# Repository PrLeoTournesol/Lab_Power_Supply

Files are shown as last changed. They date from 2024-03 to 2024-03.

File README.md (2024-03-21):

# Lab Power Supply

## Overview

The goal is to create an inexpensive laboratory power supply with stable voltage and medium/high current output. I will use an old but working power supply, the _API2PC23_ from IBM. Due to its peculiar shape, the 3D files I created might not be suited for every power supplies but can be easily adapted.   

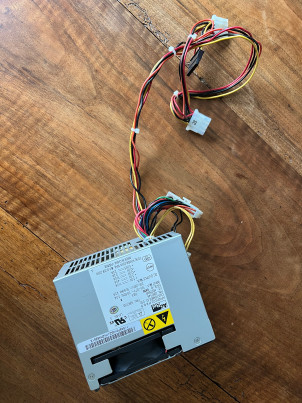
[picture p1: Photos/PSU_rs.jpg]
API2PC23


## Bill of  materials
| Name             | N°  | Link                                                      | Price (€) | Desc.                          |
|------------------|:---:|-----------------------------------------------------------|:---------:|--------------------------------|
| ATX PSU          | 1   |                                                           |           | Recycled power supply          |
| Load Resistor    | 1   | [Link](https://aliexpress.com/item/1005002006427812.html) | $\sim 3$  | 50W 6 $`\Omega`$    Load Resistor|
| Button           | 1   | [Link](https://aliexpress.com/item/32840360301.html)      | $\sim 2$  | Buttons + caps                 |
| Display          | 3   | [Link](https://aliexpress.com/item/1005006160585749.html) | $\sim 5$  | Display for voltage & current  |
| Banana plug      | 3x2 | [Link](https://aliexpress.com/item/1005005988853903.html) | $\sim 2$  | Banana plugs (link for 10)     |
| Fuse holder      | 3   | [Link](https://aliexpress.com/item/4000126701820.html)    | $\sim 2.5$| (link for 10)                  |
| Fuse             | 3   | [Link](https://aliexpress.com/item/1005004114014014.html) | $\sim 4$  | 3x10A $\quad $(link for batch) |
| USB port         | 1   | [Link](https://aliexpress.com/item/1005004550370249.html) | $\sim 7$  | 60W USB C (PD) + A (QC 3.0)|

__Total price__ : $\ \sim 25.5\ €$

I also suggest using connectors such as :
- [Type 1](https://aliexpress.com/item/1005005196465737.html)
- [Type 2](https://aliexpress.com/item/1005005283085015.html)    

The type 2 will be especially usefull for connecting to the banana plugs and fuse holders.

## Schematics

I made schematics for this project : [here](Schematics/Schematics.pdf)    

## 3D files

You can find the 3D step files I made in the Hardware folder. Please feel free to use them directly or adapt them to the power supply you are using.    
I printed the whole housing in "Ruby red" PLA, it took around 9h total with a .3mm layer height.

## Step 1 
The first step is to divide the cables comming out of the power supply depending on their voltage output. The colors are usually standardized but I would still recommand checking with a multimeter.    

- Used cables :
    - Black &emsp; &emsp; &rarr; &emsp; GND
    - Yellow &emsp; &ensp; &rarr; &emsp; +12V  @ 10A
    - Red &emsp; &emsp; &nbsp; &rarr; &emsp; +5V @ 10A
    - Orange &ensp; &nbsp;&nbsp; &rarr; &emsp; +3.3V @ 4A
    - Green &emsp;&emsp; &rarr; &emsp; Power on/off

- Unused cables :
    - White &emsp; &ensp; &rarr; &emsp; -5V
    - Purple &emsp; &ensp; &rarr; &emsp; +5VSB
    - Grey &emsp; &emsp;  &rarr; &emsp; PG
    - Blue &emsp; &ensp; &nbsp; &rarr; &emsp; -12V
    - Green &emsp;&emsp; &rarr; &emsp; Power on/off

| :zap:        Do not open the power supply ! It can be dangerous ! |
|-------------------------------------------------------------------|

I also added the load resistor between +5V and GND.

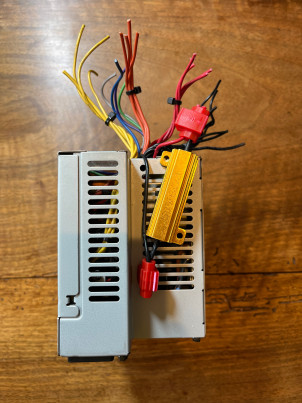
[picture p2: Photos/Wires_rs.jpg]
Wires


Every pack of wire will be connected together.

## Step 2

Prepare the different cables. I used the type 2 connectors with a pair of pliers adapted for those and simply connected the cables to the tabs on the banana plugs and fuse holders.

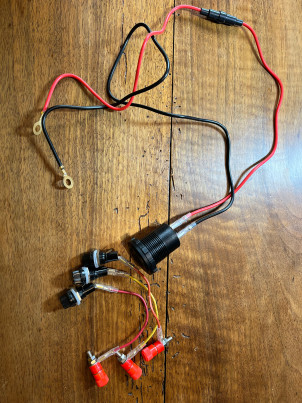
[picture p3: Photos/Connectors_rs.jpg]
Connectors


To connect the display a recommand following the schematics I made. For this I soldered the wires together with the provided connectors. 
If the wires are not the same as the one I used, please refer to the documentation of your display to avoid damaging it.
Furthermore, I connected all the displays to the +5V as a main power supply as the +3.3V would not have been enough to power them.     
To turn on the power supply, the green wire (POWER_ON/OFF) needs to be shorted to GND, hence the button.

## Step 3
Once everything is prepared and the housing 3d printed, it is assembly time !

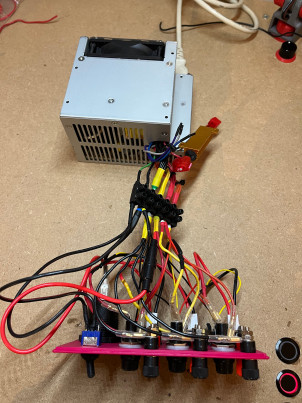
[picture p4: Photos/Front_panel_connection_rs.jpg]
Front panel


(Do not refer to the picture for wiring)

I then glued the front panel to the rest of the build. If you don't have clamps you can use rubber bands to hold everything in place while the glue dries. 

## Step 4
Enjoy the final product !

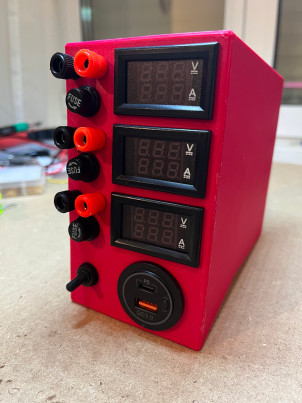
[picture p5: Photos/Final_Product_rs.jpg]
Final product


## Additionnal features

I plan to upgrade this power supply in the future with :
- Elements on the sides to hold wires that can connect to the power supply and the main cable
- Make a small dependency that can connect on the +12V with a boost converter and could ouptut any tension between +5V (?) and +24V (?)

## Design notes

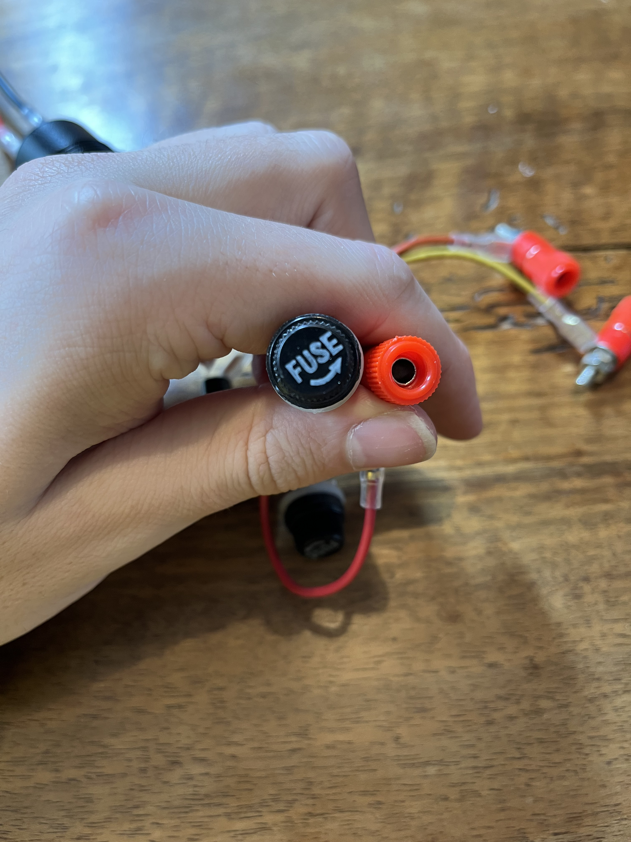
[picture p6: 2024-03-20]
Photos/Fuse.JPG

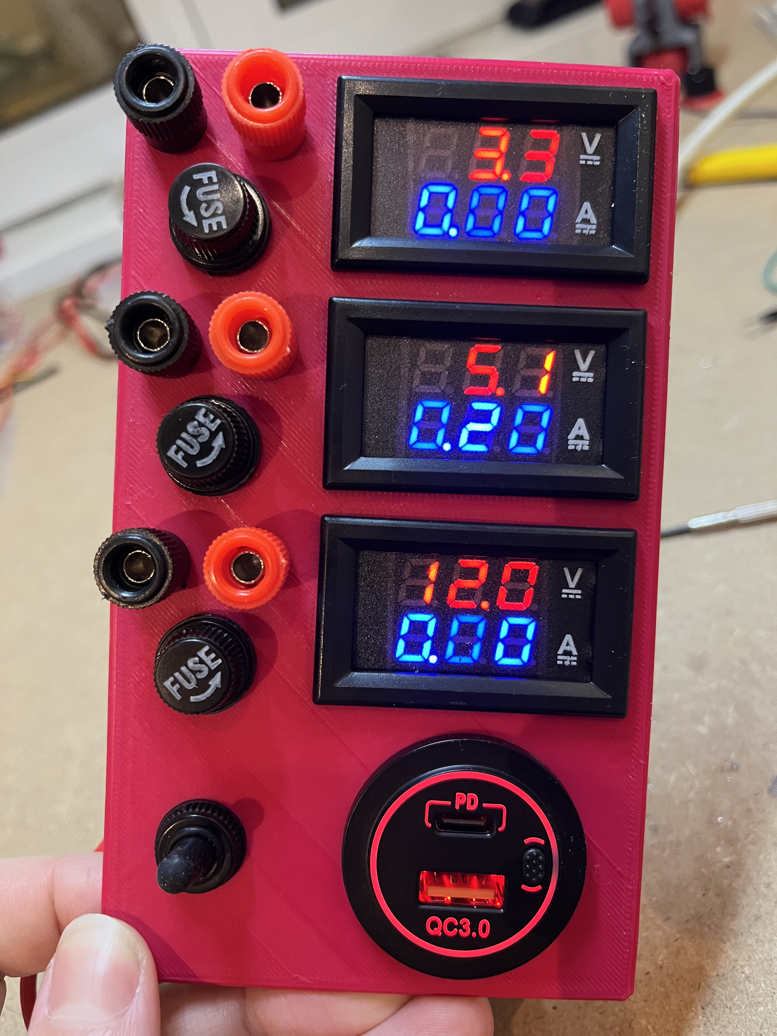
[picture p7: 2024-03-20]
Photos/Front_Panel.JPG

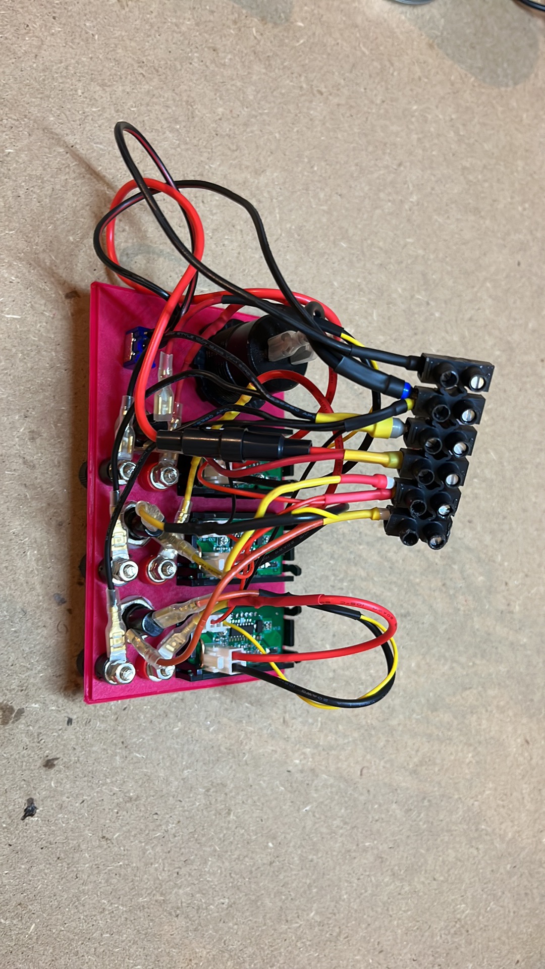
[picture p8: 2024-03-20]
Photos/Wire_Mess.JPG

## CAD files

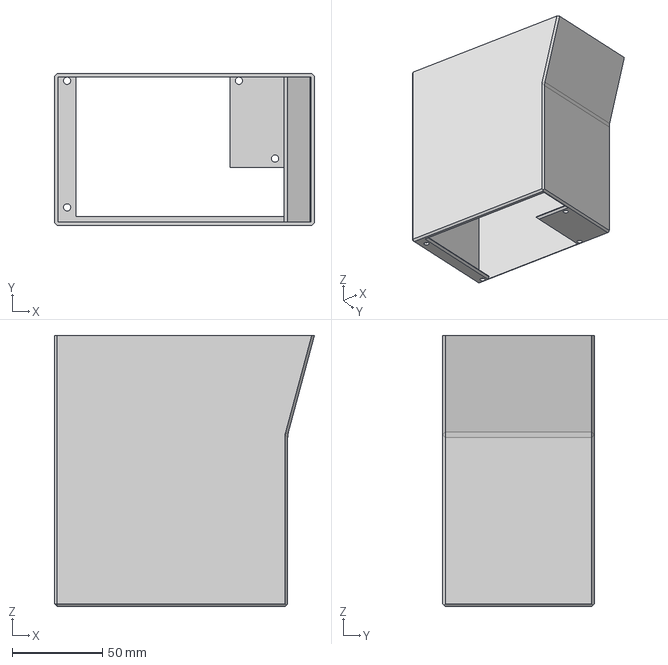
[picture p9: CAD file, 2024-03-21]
Hardware/Box.step
143.8 x 84.0 x 150.0 mm

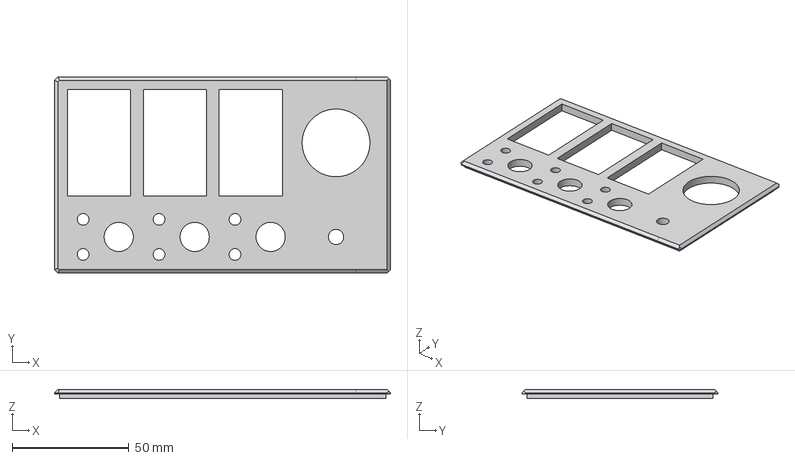
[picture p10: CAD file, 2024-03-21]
Hardware/Lid.step
143.8 x 84.0 x 4.00 mm

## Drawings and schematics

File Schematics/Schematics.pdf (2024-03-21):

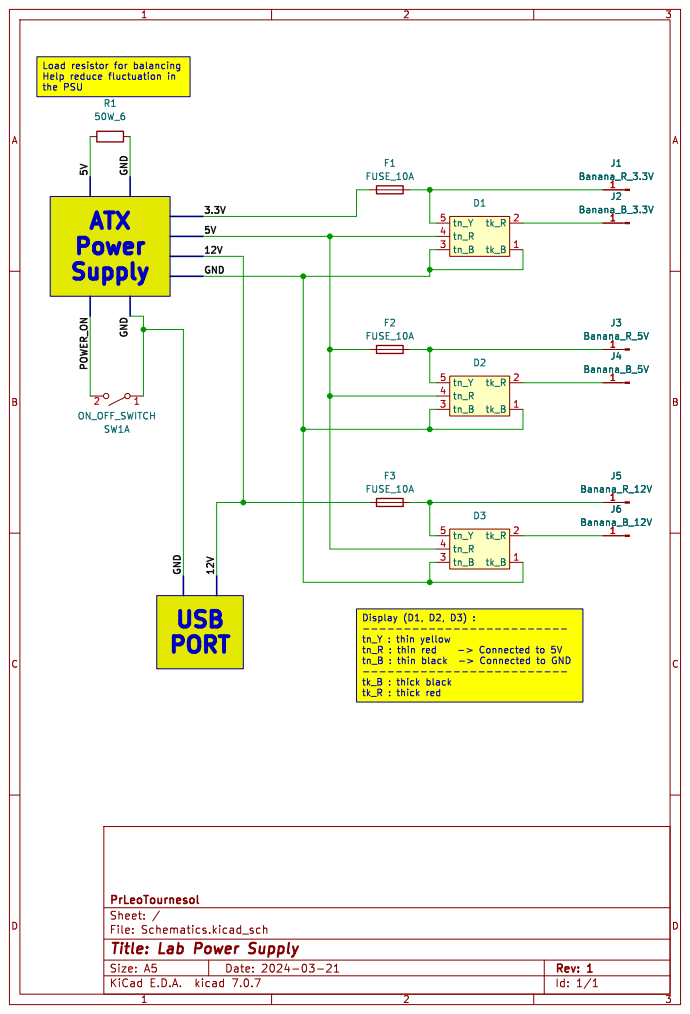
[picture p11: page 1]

File: Schematics.kicad_sch Sheet: / PrLeoTournesol

Id: 1/1 Title: Lab Power Supply
